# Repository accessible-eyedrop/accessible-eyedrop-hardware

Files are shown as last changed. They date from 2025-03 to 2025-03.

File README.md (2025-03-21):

# How to replicate the hardware prototype 

## Bill of Materials (BOM)
BOM overview

| name | link | count | price (USD) | notes |
|------|------|------|-----------|------|
| main body | [main body stl file](./3d%20print/main_body.stl) | 1 | - | - |
| eye cover | [eye cover stl file](./3d%20print/eye_cover.stl) | 1 | - | - |
| buzzer breakout board | [ebay link](https://www.ebay.com/itm/305955752072?chn=ps&mkevt=1&mkcid=28&google_free_listing_action=view_item&srsltid=AfmBOooTWdsfTm2qaCUZ0KN5gp1MGYCG-ywpCDCLxHKUqmNwkQ4iUdZ5WcI&gQT=1) | 1 | 5 | I couldn't find an identical one with the one we are currently using, but they all have same functions, size might be different though (might need to tune the nut hole position on the model) |
| ULN2003 28BYJ-48 4-Phase Stepper Motor with 5V Drive Board  | [amazon link](https://www.amazon.com/HiLetgo-ULN2003-28BYJ-48-Stepper-4-phase/dp/B00LPK0E5A/ref=sr_1_2_sspa?crid=1XHCUUF2E3X4M&dib=eyJ2IjoiMSJ9.Qa3CQUjLdgK6uEHpJhtsnI4ELhK7aHAmd-Ei-JAIRqwDcgL3MP0jscRJUTv3cKjKcBRCnk-Q7GVspk43Qe8rUQP2nwb3NTHoLz0R-nqRW-dbdu9dGK0bBUo0jIVyk2WR-lCtgC1KOEy-v6HLVw3tZP6WZ8c8Hh8UiAngDsl0kx1G1Oz0HuT1gkcUJOwoWInF0Qb-iBOIGM-bPVyV-Yh9MbHfmroCl83ngP7WWGdxIuc.V_qLAbR4rCg8FhxQB-BSsO2m62YArM6y9rSkkS14W18&dib_tag=se&keywords=stepper+motor&qid=1742525372&sprefix=stepper%2Caps%2C182&sr=8-2-spons&sp_csd=d2lkZ2V0TmFtZT1zcF9hdGY&psc=1) | 1 | 3/ea | - |
| button | [amazon link](https://www.amazon.com/Momentary-Pushbutton-Switches-Breadboard-Electronic/dp/B09R47N37H/ref=sr_1_2_sspa?crid=2PVUKEP7O3VC2&dib=eyJ2IjoiMSJ9.ndHYGnPty7Kigws1fmGVdS7mRoukyXE7d63GLZ_hPPK9dLiNlTwhgF_sj0441s5w8vsBjXUk48myqWxTyRJQZ048o0_GD2XIvtkC0UBQiazjGazZajKKhCmDU06U0MY5EPsAjLWrm_g3YfDlUAfDWL1_BALPKwt-_CScsWKJ-VUsRrbseiKehKE0JtI_NkxAVQva4WXRqfK-mgPPKOnRskIaA97SVGRYqYHc5EPSDt8.IlHTbI8hQGxLWxUMJ-KIS1Y57kifym9cBPhJpIPpoq4&dib_tag=se&keywords=button+arduino&qid=1742525424&sprefix=button+arduin%2Caps%2C254&sr=8-2-spons&sp_csd=d2lkZ2V0TmFtZT1zcF9hdGY&psc=1) | 1 | 0.05/ea | - |
| 2mm pitch lead screw & nut | [amazon link](https://www.amazon.com/400mm%EF%BC%8815-75-Inches%EF%BC%89Tr8x2-Thread-Printer-Machine/dp/B08JLWHG9H/ref=sr_1_2_sspa?crid=204RM7BHWRJDU&dib=eyJ2IjoiMSJ9.eCMHWpjfsRVtDdcYgs-M-BNH6PpmcOsWporfgeZVTfzGjHj071QN20LucGBJIEps.0hwz7vzlM7jpEtuQBS2sCe4ikMdKQQbqaFn-zhjBUyg&dib_tag=se&keywords=2mm%2Bpitch%2Blead%2Bsc&qid=1742525536&sprefix=2mm%2Bpitch%2Blead%2Bsc%2Caps%2C358&sr=8-2-spons&sp_csd=d2lkZ2V0TmFtZT1zcF9hdGY&th=1) | 7.5/ea | 1 | cut the lead screw to about 2mm in length |
| LED strip | [amazon link](https://www.amazon.com/PAUTIX-Dimmable-Backlight-Flexible-Lighting/dp/B0B1J57XS9/ref=sxin_16_pa_sp_search_thematic_sspa?content-id=amzn1.sym.9ae96427-feac-4323-af17-06872169e170%3Aamzn1.sym.9ae96427-feac-4323-af17-06872169e170&crid=3636KKS2ZFGPG&cv_ct_cx=led%2Bstripe&keywords=led%2Bstripe&pd_rd_i=B0CMSW9CLB&pd_rd_r=f08adace-8df2-4b1c-a126-9ee66ef9e448&pd_rd_w=DWOXe&pd_rd_wg=lcmzB&pf_rd_p=9ae96427-feac-4323-af17-06872169e170&pf_rd_r=QQ8V7F31ANWMCMHZ00FK&qid=1742525622&sbo=RZvfv%2F%2FHxDF%2BO5021pAnSA%3D%3D&sprefix=led%2Bstrip%2Caps%2C168&sr=1-2-e169343e-09af-4d41-85b1-8335fe8f32d0-spons&sp_csd=d2lkZ2V0TmFtZT1zcF9zZWFyY2hfdGhlbWF0aWM&th=1) | 14 | 1 | cut the strip to about 80mm long |
| battery box | [amazon link](https://www.amazon.com/Goweewon-AA-Battery-Holder-Leads/dp/B0CWFCPNRT/ref=sr_1_1_sspa?crid=1BZVWJBU2P0O2&dib=eyJ2IjoiMSJ9.lPPObmwoituHQda3Go8YDFV8ebSSTyZxt66x-IetRj_hKv14Mnir7D-SfcK-wCoWtLUmV6zvzdw5PuHcHJaY7MemG5b2BceWZ9UIweKUhf32ZWgmLkdKqdtDxQIeu-vlzh7K4wiMqztejkwGbNzGfzw3psh4TJhmev0YHCil9VHlyvsPq2FWLtYwCZ174DDn7JDUrAo0xSAeMPqTaIWuUhKquB9LYulQ8k4IOMf3A8Y.FzgQ_xxLh6hHwV1t9o3UPgbwFwJuESdmFnRjs8NJuQs&dib_tag=se&keywords=battery%2Bbox%2BAA%2B3%2Bslot&qid=1742525910&sprefix=battery%2Bbox%2Baa%2B3%2Bslot%2Caps%2C146&sr=8-1-spons&sp_csd=d2lkZ2V0TmFtZT1zcF9hdGY&th=1) | 8 | 1 | for powering the LED strip (which should run under 5V), this battery box provides 4.5V, but still sufficient to light up the LED |
| 9v battery connector | [amazon link](https://www.amazon.com/Battery-Connector-Plastic-Experiment-Equipment/dp/B08SL9X2YC/ref=sr_1_2?crid=1GCFFCX99NKSW&dib=eyJ2IjoiMSJ9.cPyl9XTIX6B9MfgCRRpDEscYkyho57s4B7exQhpIL-wI_QNpAo54rJSOgmafsjfW_Ptu-K4pbwMHh_RQRAcoM-qAH1VsWwa5F2jPNfGELzU94uKM4MY-qSdgPqUV7puHugXNUwtQ1OY0gwNrjQkRP2ly-SyBEw27NWmWeYhdyz8YrocmLrzZtNvaezwpyE_kb14BB1pTysETQUgGfqA-QXR0EVs7DLFyquBVsagrAkE.kGZOCUJ6Tx3glwoQO8jcU-lht6wefbUxfDBtPC57_jA&dib_tag=se&keywords=9v%2Bbattery%2Bcap&qid=1742528843&sprefix=9v%2Bbattery%2Bc%2Caps%2C278&sr=8-2&th=1) | 0.5/ea | 1 | for connect to 9v battery and power the stepper motor drive board |
| toggle switch | [amazon link](https://www.amazon.com/HiLetgo-AC125V-Terminals-Position-Toggle/dp/B079JBF815/ref=sxin_17_pa_sp_search_thematic_sspa?content-id=amzn1.sym.9ae96427-feac-4323-af17-06872169e170%3Aamzn1.sym.9ae96427-feac-4323-af17-06872169e170&crid=1HUDVM364L41R&cv_ct_cx=toggle+switch&keywords=toggle+switch&pd_rd_i=B079JBF815&pd_rd_r=8f64b633-7c90-412f-becf-72ffd5faf14f&pd_rd_w=5qhhp&pd_rd_wg=kfm2i&pf_rd_p=9ae96427-feac-4323-af17-06872169e170&pf_rd_r=ZC2FM8ZFB2CQ5SD7E86Z&qid=1742528935&sbo=RZvfv%2F%2FHxDF%2BO5021pAnSA%3D%3D&sprefix=toggle+switch%2Caps%2C193&sr=1-4-e169343e-09af-4d41-85b1-8335fe8f32d0-spons&sp_csd=d2lkZ2V0TmFtZT1zcF9zZWFyY2hfdGhlbWF0aWM&psc=1) | 0.6 | 1 | toggle whether the 9v battery is connected to the stepper motor drive board |
| Raspberry Pi Camera Module V2-8 Megapixel | [amazon link](https://www.amazon.com/Raspberry-Pi-Camera-Module-Megapixel/dp/B01ER2SKFS/ref=sr_1_3?dib=eyJ2IjoiMSJ9.SdZxeeuAaWgC9GeoeEJUFP62foW2SztM96rrEg7VSsYD-p1fQE48UWVjERlWaOfWzhD-QO70AYkKt6meJD3UZqbjvM337zp8JJ6E8cCavg-oFdH4X9n6Cc0zgie6v2GYe3G624QvkwQyoZj3dIts3Fc4AASXSf19Jx852MXh_J98LPWiijeyERAfjZTtMTasm-vw5YwcjXoSd08cym7TBl4mqm_aLJgTqAVmBJaZ7Xg.3ECh9_-607HgW_VnJy7emLPYlaDEs5zsGDzYKBbPsto&dib_tag=se&keywords=raspberry+pi+camera&qid=1742529031&sr=8-3) | 13 | 1 | - |
| Raspberry Pi 4B | [amazon link](https://www.amazon.com/Raspberry-Model-2019-Quad-Bluetooth/dp/B07TC2BK1X/ref=sr_1_1?crid=1YITJHF9OCVYQ&dib=eyJ2IjoiMSJ9.HavuMzOx0pibLLpdWCmY00k6Sz1h7IjNXYchbCG7xmeterViSIylhvpNrT0tJWntAAZEUi1P3KQ2hMqRN-N16KH3eKSnNiwrf_Aae9l2NKCRTKlflgkhkYDdPe46vN3sP5cyneKBqcfOM0E_Xj3jhQTZ-OXSbg2ufINEuSbhWTwDLKidwPub9YLdA_p0K_DCgFsNITO8G_auXlTd4idIkvWbkBjNhewNp05Cuu8sWQM.rv6nShqwJBonCcP8Fnxt4ksp6jPn3jQPqRsCoRnEDFM&dib_tag=se&keywords=raspberry%2Bpi%2B4b&qid=1742529069&sprefix=raspberry%2Bpi%2B4%2Caps%2C312&sr=8-1&th=1) | 62 | 1 | - |
| Refresh Optive Advanced Eye Drops | [amazon link](https://www.amazon.com/Refresh-Optive-Advanced-Fluid-Ounce/dp/B00B6A6VFQ/ref=sr_1_5_sspa?crid=7ERC7EVXXWKJ&dib=eyJ2IjoiMSJ9.qTPlK5IAgLBEWNLgtoHNdzhDvRqCOJkCKJrL3bf_h0xcisQixgUrKDPuMVApe4HTqO_JldvpJq1fVso6dUAFhEOxAfksLIddEE_4GHl6UMaoY-DZp1IXFQAtzvPaz64osiQBRxVo0ng5Pmq3PItP3Y8OvjsA-MsQMrnIH7Ka5YwmobsPoc6AfNDXd9DPhmphNonJ8fAS1HmKC8C42gbgxUxyUALSHOtz99r_RsnOsMjRJCqlNoB4jukNvIUZJjdUbYGaTj-JPnDY74fr5uCdHggc4wQm-qd4ilJtiwszkoY.2t2YM7Hj7KLM5Sm8xaArdgFA96zQGDwFfv3uAjP7w78&dib_tag=se&keywords=eyedrop&qid=1742529148&rdc=1&sprefix=eyedrop%2Caps%2C244&sr=8-5-spons&sp_csd=d2lkZ2V0TmFtZT1zcF9hdGY&psc=1) | 10/ea | 1 | - |

## Assemble

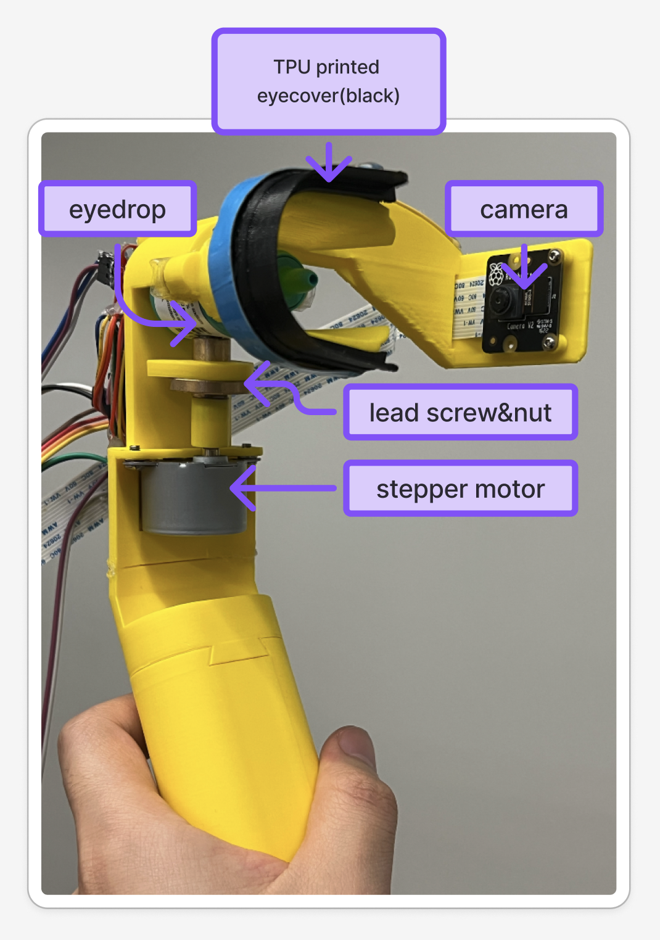
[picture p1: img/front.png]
front view

1. The stepper motor is fixed to the main body with M3 nut and screw.
2. The lead screw nut is bound with a tab, then connected with the rod of the stepper motor with a 3d printed adaptor. The lead screw nut should be placed against the eyedrop bottle.
3. Place the eyedrop bottle into the slot of the main body.
4. On the eyecover side, attach the TPU-printed eyecover (friction fit) and the camera module (connected with M3 screw and nut). Then the eyecover should be able to be snap fit to the neck of the eyedrop bottle.
5. Attach 7mm diameter magnet to both the main body and the eyecover. This allows the eyecover to rotate 180deg and fix into the right position leveraging magnet attraction. 

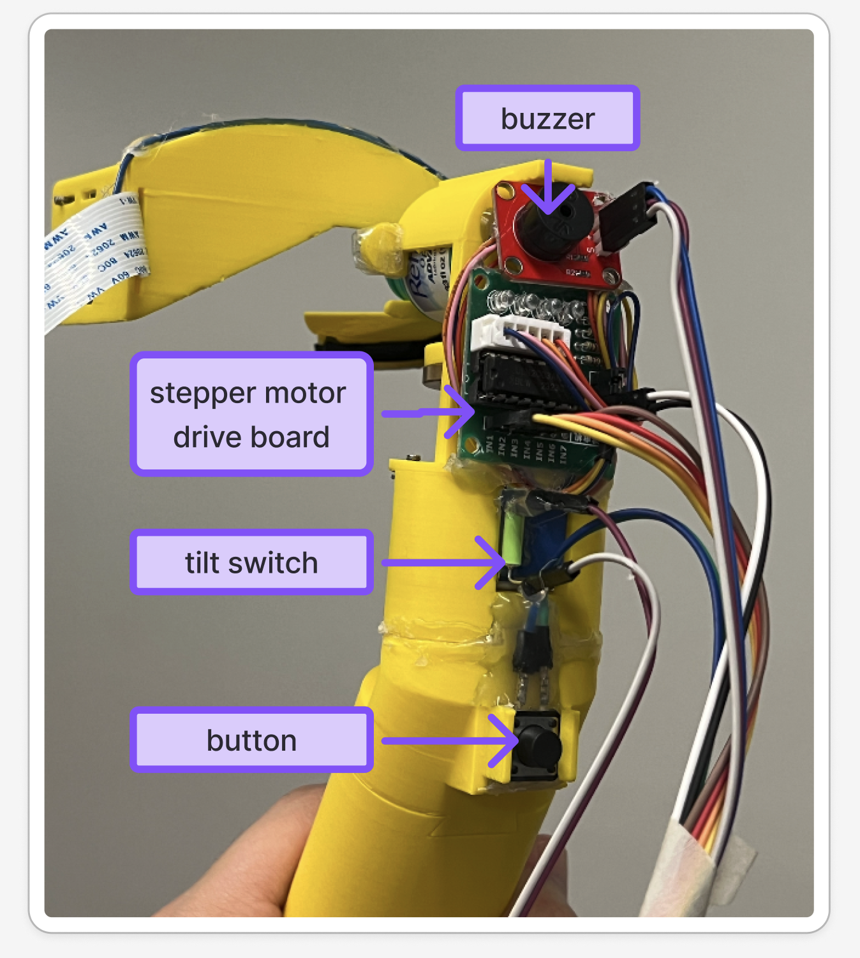
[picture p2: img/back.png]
back view

1. Buzzer module, motor drive board module, and button are all hot glued onto the device. (In our new fusion design, they can attach to the device using M3 nuts and screws.)
2. Buzzer module connection to Rasp Pi: `signal -> GPIO23`, `Vcc -> 3V3`, `GND->GND`
3. Motor driver module connection to Rasp Pi: `IN1 -> GPIO17`, `IN2 -> GPIO18`, `IN3 -> GPIO27`, `IN4 -> GPIO22`. 9V and GND of the driver board is connected to the 9V battery connector (with the toggle switch connected in serial).
4. Button connection to the Rasp Pi: `Button Pin1 -> GPIO4`, `Button Pin2 -> GND`.

# How to use the prototype

1. After full assembly, clone the python code from https://github.com/accessible-eyedrop/accessible-eyedrop-RaspPi to the Rasp Pi, follow the instruction in the repo to run the code on the Pi.
2. Toggle on the LED strip and stepper motor power supply.
3. Place the device over your eye, tilt your head backwards.

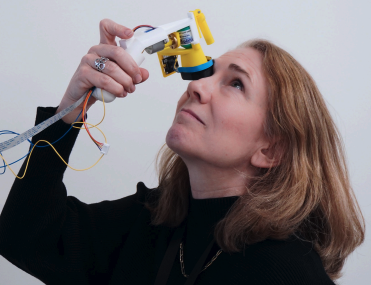
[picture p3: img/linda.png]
use instruction


4. Push the button, the device should dispense one drop, and the Python backend will tell you whether it is a successful administration or not. If you also run our front-end code https://github.com/accessible-eyedrop/accessible-eyedrop-Frontend, the data can be shown on the front-end.

HOW-TO-USE video [demo1](./video/dispense.mp4) and [demo2](./video/workflow.mp4).

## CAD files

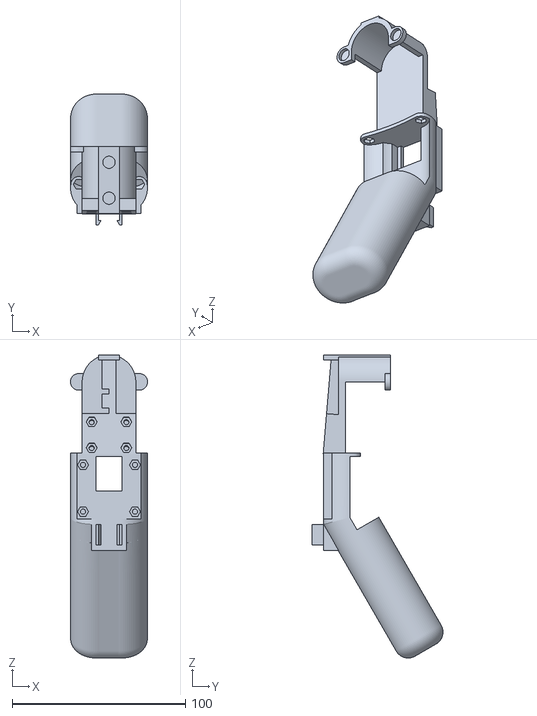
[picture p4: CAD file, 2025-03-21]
3d print/main_body.stl
44.6 x 75.7 x 175.1

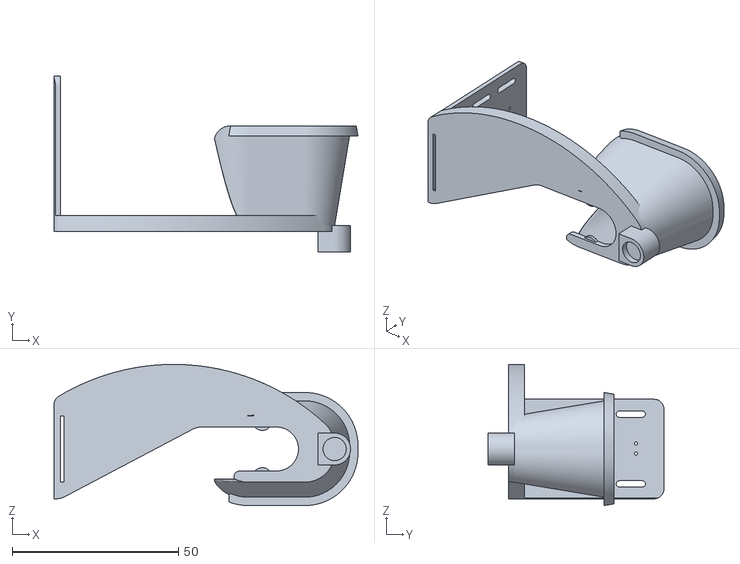
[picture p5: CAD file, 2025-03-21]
3d print/eye_cover.stl
91.5 x 53.0 x 42.5

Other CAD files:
smartdrop.f3d

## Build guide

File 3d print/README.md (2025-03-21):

- `main_body.stl`: the stl file for the main body of the device
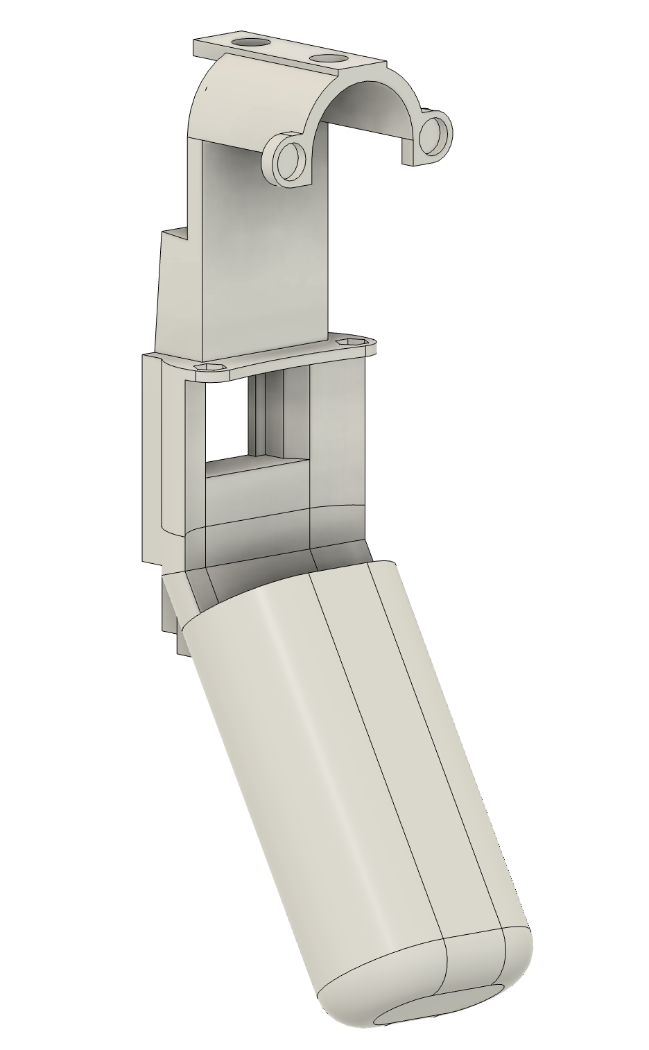
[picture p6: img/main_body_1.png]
Main body view 1

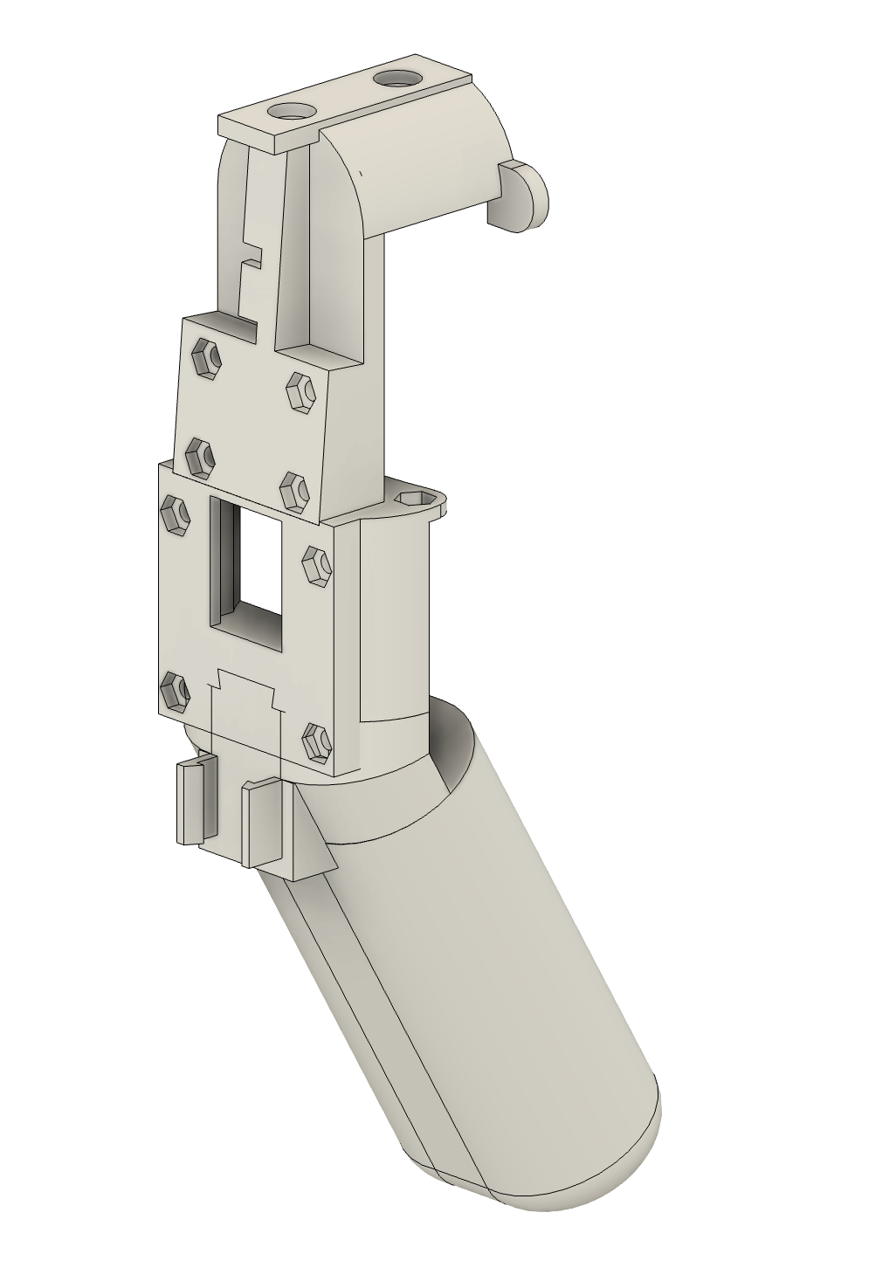
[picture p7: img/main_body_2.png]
Main body view 2

    
- `eye_cover.stl`: the stl file for the eye cover piece of the device
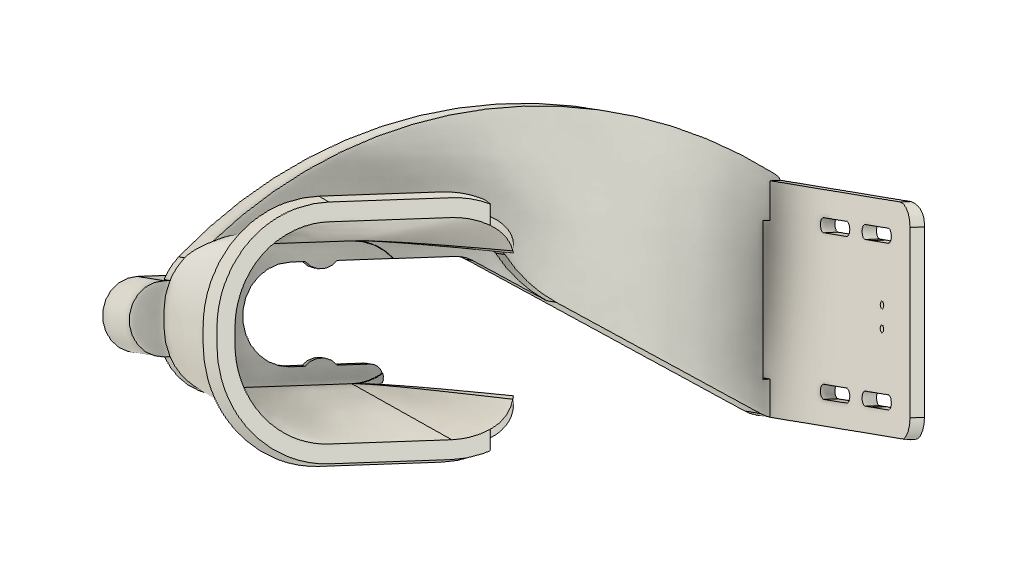
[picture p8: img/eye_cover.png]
eye cover


## Video Demo
Video Demo
